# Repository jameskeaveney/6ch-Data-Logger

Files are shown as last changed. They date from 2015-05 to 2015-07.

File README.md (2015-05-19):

# 6 channel data logger using Arduino DUE and python
A six-channel data logger running on the Arduino DUE, that sends data via SerialUSB to a PC. Python is used to grab this data, process it and save it.

Original purpose is as a slow multi-channel data logger for use with a DFB laser, where 
a frequency sweep is controlled via temperature tuning. A digital pin is used, with an external
potentiometer, to set the magnitude of the temperature sweep (the onboard DAC could have been used,
but the adjustment range is only 1/6 to 5/6 of the full 0 - 3V3 range). The temperature is swept
by switching the state of the digital pin, which in turn changes the setpoint on the external
temperature controller (Thorlabs TED200C). Since the temperature scan is slow (~90 seconds), and 
we need lots of channels, a normal oscilloscope isn't the best for this job.

Photodiode signals from the main experiment vapour cell, two reference cells (one at zero field,
one at 0.6 Tesla), Fabry-Perot etalon, a laser power monitor photodiode, and the temperature
monitor (actual temperature, rather than setpoint) are required.

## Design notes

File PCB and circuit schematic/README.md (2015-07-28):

Schematic and PCB layout produced using RS DesignSpark v7.0 (http://www.rs-online.com/designspark/electronics/eng/page/designspark-pcb-home-page)

Circuit is essentially takes all inputs through unity gain buffers (as a crude over-voltage protection for the arduino ADC pins). Output goes through Arduino DUE DAC0 into a potential divider and fixed gain amplifier, for 0-5V operation.

All components are through-hole, for ease of soldering.

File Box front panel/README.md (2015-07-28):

Autodesk Inventor drawings for a basic front panel design including 9 BNC (8 input, 1 output) and 1 USB-B connector for powering the Arduino inside.

The USB-B panel mount connector has an internal cable with a Micro-USB (male) connector on the other end, and can be bought (very cheaply) from here:

http://www.hobbytronics.co.uk/cables-connectors/usb-connectors/usb-panel-cable-b-microb

The panel is designed around this housing:
http://onecall.farnell.com/hammond/1455t2201bk/case-aluminium-52x160x220mm/dp/1511228

The internal mount has 4 screw holes for the arduino via 4 M2.5 standoffs. It is designed to fit into the slots of the enclosure.

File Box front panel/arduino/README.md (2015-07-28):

Arduino DUE CAD design credit to Babu George, available here:

https://grabcad.com/library/arduino-due-1

(I'm unaware of any license files, please let me know if there are any issues)

Imported into Autodesk Inventor 2015 to create .ipt files

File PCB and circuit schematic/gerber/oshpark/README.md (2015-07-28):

Gerber files output from DesignSpark

Formatted for OSHPark.com PCB fabrication - see https://oshpark.com/guidelines for details on file extensions

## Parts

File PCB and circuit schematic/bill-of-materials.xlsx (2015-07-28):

Part Name | Specific Type | Number required | Farnell Part Number
0.1" PCB Header, Male | 20x1 | 1 | 1022262
 | 3x1 | 1 | CN14488
0.1" PCB Header, Female | 2x1 | 9 | CN14529
Op Amp | OPA2350 | 5 | 1097444
Resistor | 100kOhm | 9 | 1127906
 | 10kOhm | 1 | 9338373
 | 20kOhm | 1 | 2329754
Capacitor | 0.1uF | 5 | 2395773
 | 1uF | 1 | CA05952
Trim Pot | 100kOhm, 20 turn | 1 | 1304529
Instrument Box | - | 1 | 1511228

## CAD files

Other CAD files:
Box front panel/Front-panel.dwg
Box front panel/mount.dwg
Box front panel/OldVersions/mount.0001.dwg
Box front panel/Front-panel.ipt
Box front panel/OldVersions/Front-panel.0006.ipt
Box front panel/OldVersions/mount.0001.ipt
Box front panel/OldVersions/standoff.0002.ipt
Box front panel/arduino/Imported Components/ARDUINO DUE/ARDUINO DUE.iam
Box front panel/arduino/Imported Components/ARDUINO DUE/ARDUINO DUE.ipt
Box front panel/arduino/Imported Components/ARDUINO DUE/Berg Header - 1.27 x 10.ipt
Box front panel/arduino/Imported Components/ARDUINO DUE/Berg Header - 2.54 x 2.ipt
Box front panel/arduino/Imported Components/ARDUINO DUE/Berg Header Receptacle 2.54 x 10 - FCI - 66951-010LF.ipt
Box front panel/arduino/Imported Components/ARDUINO DUE/Berg Header Receptacle 2.54 x 36 - FCI - 66953-018LF.ipt
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

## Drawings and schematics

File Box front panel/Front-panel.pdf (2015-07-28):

## DETAIL A SCALE 2 : 1

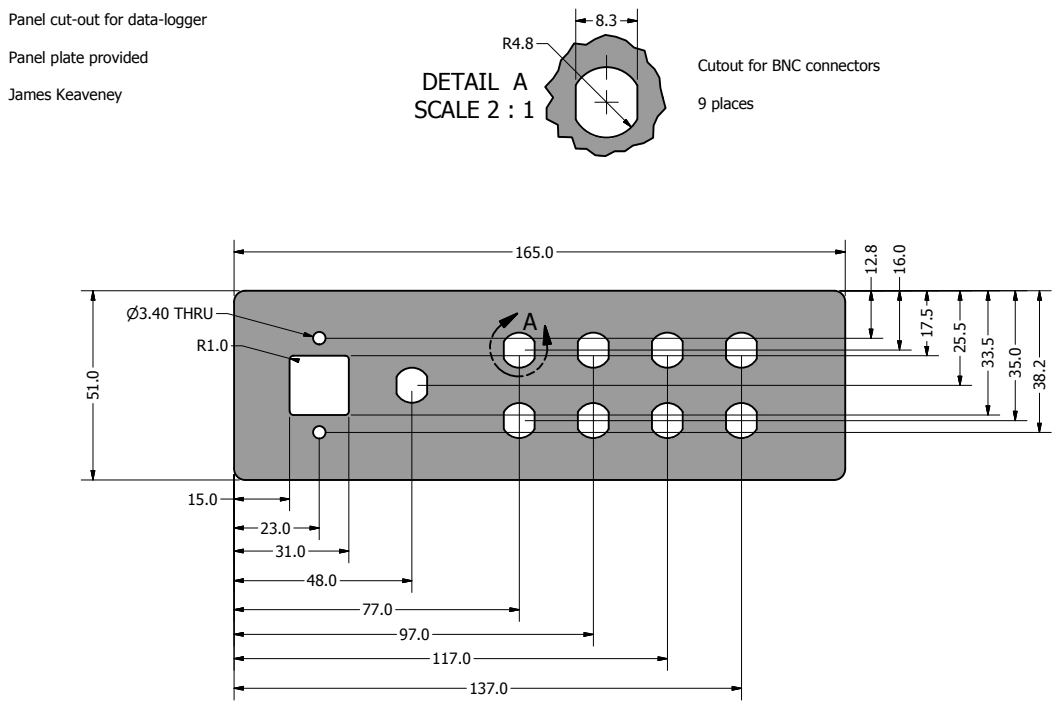
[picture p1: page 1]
James Keaveney; 9 places; P3.40 THRU

Panel cut-out for data-logger

Panel plate provided

Cutout for BNC connectors

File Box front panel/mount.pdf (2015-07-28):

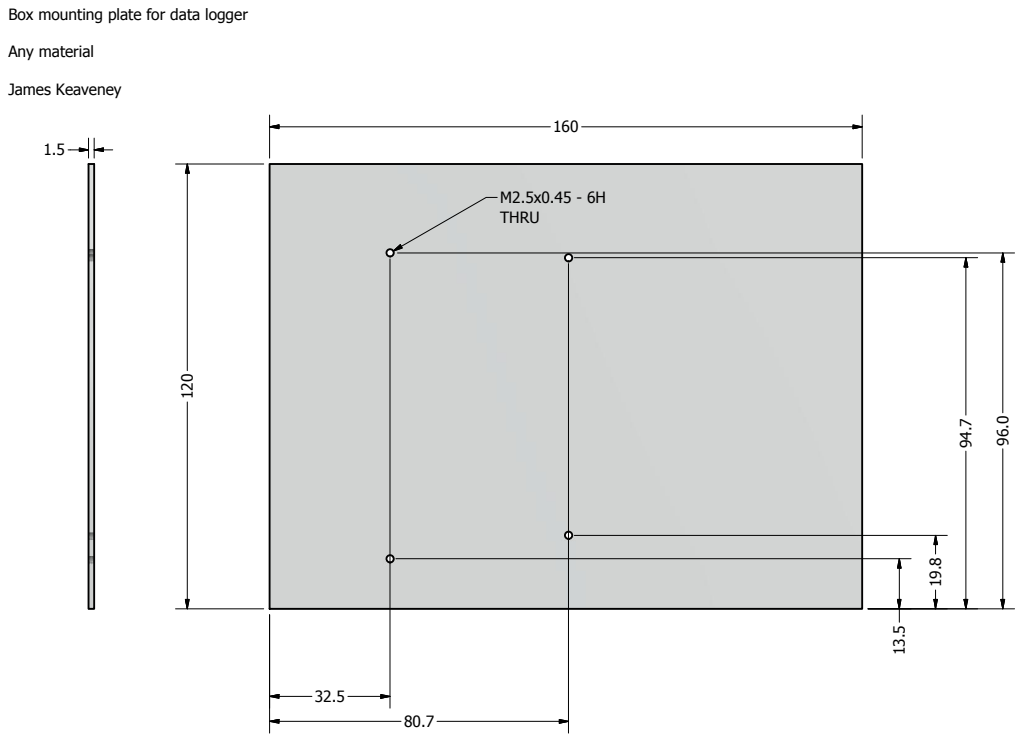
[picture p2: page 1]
M2.5x0.45 - 6H THRU; Any material; James Keaveney

Box mounting plate for data logger

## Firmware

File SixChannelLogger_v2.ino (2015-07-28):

/*

Six channel data logger using Arduino DUE.

**
Original purpose is as a slow (~kS/s) multi-channel data logger for use with a DFB laser, where 
a frequency sweep is controlled via temperature tuning. The on-board DAC is used, with an external
amplifier (gain adjustable), to alter the setpoint of a Thorlabs TED200C temperature controller. 
Since the temperature scan is slow (~30 seconds), the temperature controller PID can follow the setpoint
in nearly real-time. Since we need to record lots of channels, and the sampling rate isn't very high, 
a normal oscilloscope isn't the best for this job.

Input signals are from the main experiment vapour cell, main power monitor, reference cell, 
reference power monitor, Fabry-Perot etalon, and the temperature monitor (actual temperature, 
rather than setpoint).
**

Analog inputs on pins A0-A5 are read-in at an adjustable sampling rate of ~2 kS/s.
The sampling rate can be increased up to around ~16 kS/s for 6 channels, probably faster for
fewer channels [channels must be enabled/disabled by setting the registers in the setup() method below],
by adjusting the sampling_time variable

With the current PCB design, can have up to 8 input channels, which are all buffered as a simple
overvoltage protection for the ADC pins. There is no other OVP circuitry, so the op-amps will blow
if too much voltage is used!

The ADC data is buffered then sent quickly via SerialUSB. Since there is some overhead 
involved with Serial transfer, the data should be transferred in large quantities ( > 1 kB) so
as to minimise total transmission time. Buffering will be memory-limited at some point. The
largest buffer possible is currently untested!

PySerial is used to grab the data from the serial port and read it into python. For this,
the python module SixChannelReader.py has been written (in the same directory as this file), 
which provides class-based methods of reading in the data, as well as a method of 
synchronisation for triggering purposes.

************
** NOTE: the USB connection to the Arduino Due must be to the NATIVE port, not the programming port!
************



Author: James Keaveney
18/05/2015
updated 27/07/2015 - changed digital temperature control to analog temperature control with Timer ISR

*/

#include <DueTimer.h>

// set up variables
const int buffer_length = 200; // length of data chunks sent at a time via SerialUSB

const long acquisition_time = 30000; // in ms
const long settling_time_ms = 10000; // in ms
const int sampling_time = 440; // in micros (60 microsec per loop + this delay; e.g. 190 => 250micros total = 4 kS/s)

const int StatusPin = 52;

String strTime = "";
String strOut = "";
String strC1 = "";
String strC2 = "";
String strC3 = "";
String strC4 = "";
String strC5 = "";
String strC6 = "";

int dac_output = 0;

unsigned long current_time;

void setup() {
  // set up digital pin for status indicator - ON while acquiring data
  // this could be used for LED output, or as a TTL trigger for an external 'scope
  pinMode(StatusPin, OUTPUT);
  digitalWrite(StatusPin, 0);
  
  // set ADC and DAC resolution
  analogReadResolution(12);
  analogWriteResolution(12);
  
  // initialise DAC0 output and wait for temperature to settle
  dac_output = 0;
  analogWrite(DAC0,dac_output);
  dacc_write_conversion_data(DACC_INTERFACE, dac_output);


  // manually set registers for faster analog reading than the normal arduino methods
  ADC->ADC_MR |= 0xC0; // set free running mode (page 1333 of the Sam3X datasheet)
  ADC->ADC_CHER = 0xFC;  // enable channels  (see page 1338 of datasheet) on adc 7,6,5,4,3,2 (pin A0-A5)
                       // see also http://www.arduino.cc/en/Hacking/PinMappingSAM3X for the pin mapping between Arduino names and SAM3X pin names
  ADC->ADC_CHDR = 0xFF03; // disable all other channels
  ADC->ADC_CR=2;       // begin ADC conversion
  

  // initialise serial port
  SerialUSB.begin(115200); // baud rate is ignored for USB - always at 12 Mb/s
  while (!SerialUSB); // wait for USB serial port to be connected - wait for pc program to open the serial port

  // setup DAC increment period - set by acquisition time
  int timer_period;
  timer_period = acquisition_time*1000 / 4095;
  //SerialUSB.println(timer_period);
  Timer3.attachInterrupt(dac_increment);
  Timer3.setPeriod(timer_period);
  

  // allow temperature to settle first
  delay(settling_time_ms);  
}


void dac_increment() {
  // function called to increment the DAC output at regular intervals - used by timer ISR
  dac_output++;
  dacc_write_conversion_data(DACC_INTERFACE, dac_output);
}

void loop() {

  // data acquisition will start with a synchronisation step:
  // python should send a single byte of data, the arduino will send one back to sync timeouts
  int incoming = 0;
  if (SerialUSB.available() > 0) // polls whether anything is ready on the read buffer - nothing happens until there's something there
  {
    incoming = SerialUSB.read();
    // after data received, send the same back
    SerialUSB.println(incoming);
    
 
    //wait a little time for python to be ready to receive data - (not sure if this is really necessary)
    delay(50); // ms
    
    // do something to alter the temperature - start timer
    Timer3.start();
    
    // turn status/trigger on
    digitalWrite(StatusPin, 1);

    // measure start time - then acquire data for an amount of time set by the acquisition_time variable
    unsigned long start_micros = micros();
    unsigned long start_time = millis();
    while (millis() < (start_time+acquisition_time))
    {
        
      // generate and concatenate strings
      for (int jj = 0; jj < buffer_length; jj++)
      {
        
        // ADC acquisition
        
        // can put this in a small loop for some averaging if required - takes ~ 60 microsec per read/concatenate cycle
        while((ADC->ADC_ISR & 0xFC)!=0xFC); // wait for conversion to complete - see page 1345 of datasheet     
        
        // concatenate strings
        current_time = micros()-start_micros;
        strTime.concat(current_time); // time axis
        strTime.concat(',');     
        strC1.concat(ADC->ADC_CDR[7]); // read data from the channel data register
        strC1.concat(',');
        strC2.concat(ADC->ADC_CDR[6]);
        strC2.concat(',');
        strC3.concat(ADC->ADC_CDR[5]);
        strC3.concat(',');
        strC4.concat(ADC->ADC_CDR[4]);
        strC4.concat(',');
        strC5.concat(ADC->ADC_CDR[3]);
        strC5.concat(',');
        strC6.concat(ADC->ADC_CDR[2]);
        strC6.concat(',');
        
        
        //Serial.print(current_time);
        //Serial.print(",");
        
        delayMicroseconds(sampling_time); // limit sampling rate to something reasonable - a few kS/s
      }
      
      // send data via SerialUSB
      // perform a flush first to wait for the previous buffer to be sent, before overwriting it
      SerialUSB.flush();
      strOut = strTime + strC1 + strC2 + strC3 + strC4 + strC5 + strC6;  
      SerialUSB.print(strOut); // doesn't wait for write to complete before moving on
      
      
      // clear string data - re-initialise
      strTime = "";
      strC1 = "";
      strC2 = "";
      strC3 = "";
      strC4 = "";
      strC5 = "";
      strC6 = "";
    }
  
    // turn status/trigger off
    digitalWrite(StatusPin, 0);

    // stop timer
    Timer3.stop();
    
    // finally, print end-of-data and end-of-line character to signify no more data will be coming
    SerialUSB.println("\0");
    
    // reset temperature, and wait a while to allow temperature to settle
    delay(2000);
    dac_output = 0;
    dacc_write_conversion_data(DACC_INTERFACE, dac_output);
    delay(settling_time_ms);
  }
}

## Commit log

2015-07-28 PCB and circuit design
    [DataLogger_IO_Board.sch, Input Buffers - Board Outline.gbr, Input Buffers - Bottom Copper (Paste).gbr, Input Buffers - Bottom Copper.gbr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]
2015-07-28 CAD Designs for front panel and internal mount
    [ARDUINO DUE.0001.ipt, ARDUINO DUE.iam, ARDUINO DUE.ipt, Berg Header - 1.27 x 10.0001.ipt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]
2015-07-28 Added bill of materials for PCB board
    [bill-of-materials.xlsx]
